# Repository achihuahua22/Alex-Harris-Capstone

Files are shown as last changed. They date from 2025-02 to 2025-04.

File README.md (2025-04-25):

# Alex Harris Capstone: Low Cost Device for Laboratory Equipment Integration
 _This project is a Raspberry Pi Hat that is intended to receive inputs from Self-Driving-Laboratory equipment and utilize the raspberry pi to publish device data onto the network.
This repository contains all of the schematics, documentation, and code necessary to build this device._

This project builds on an-ven’s [graspib](https://github.com/an-ven/graspib) project by adding more RS232 support and a UART breakout pin. 

It also utilizes the [Linux GPIB package](https://linux-gpib.sourceforge.io)

Currently, this device supports UART, RS232, and GPIB. 

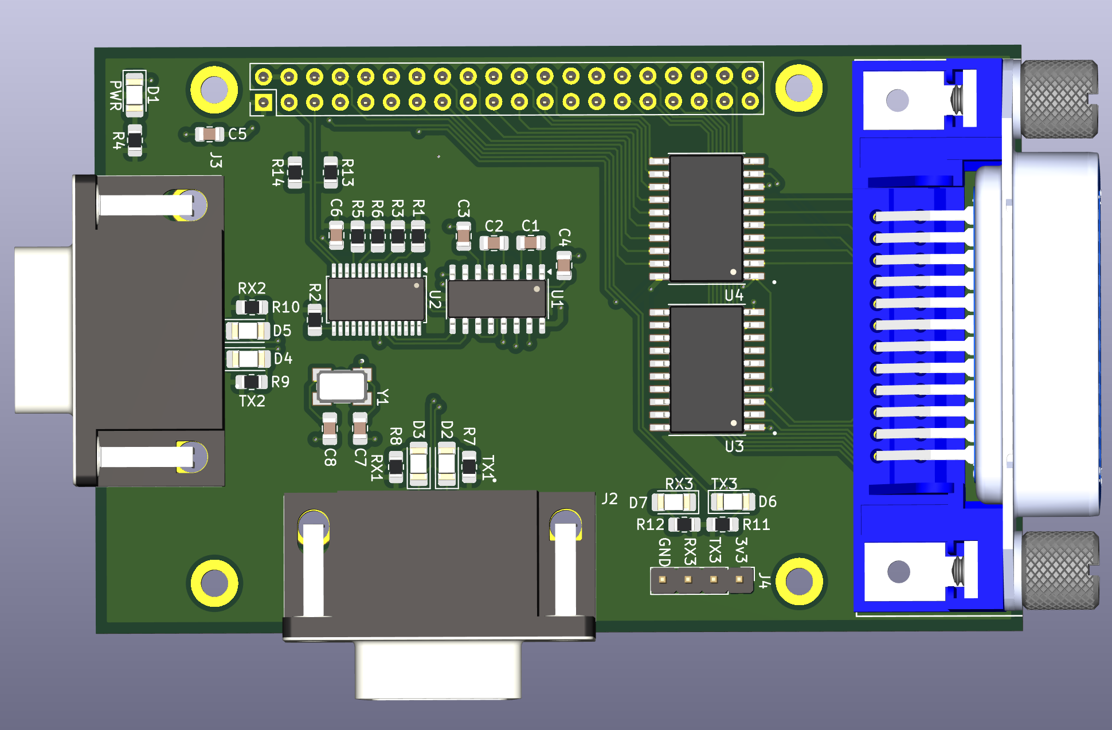
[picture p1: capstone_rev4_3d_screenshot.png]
3d model of pcb


If you want to make one yourself, the files are [here](capstone_cad_rev4)

## Introduction
This project is a Raspberry Pi Hat that is intended to 
improve self driving lab connectivity and modularity 
by allowing researchers to integrate multiple lab 
devices into their networks. I worked with Dr. Taylor 
Sparks' self-driving laboratory (SDL) to develop a 
device to more easily network with lab equipment. 
A self-driving laboratory is a laboratory where
everything from specimen handling, experiments, 
and decision making is fully automated to 
accelerate research [1]. This device intends to be an 
easy-to-use device for networking and save 
researchers money. To make a device “easy to use” I 
wanted to work with hardware that researchers are 
familiar with. This led to me choosing to design a 
board that attaches to a Raspberry Pi. 
I chose to use a Raspberry Pi based solution
because of its prevalence in the research space. 
Many pieces of university research level lab 
equipment have very little interconnection due to 
the age of the device or the type of communication 
protocol. Another issue is that products can use 
proprietary connection methods, which makes the 
task of developing an interconnected SDL very 
difficult [2]. I wanted to develop a device that can 
put data collected by lab equipment onto the 
network using a Raspberry Pi and a circuit board 
that sits on top of the Pi to handle the 
communications.

## Design
### Methods
I began with researching similar solutions to this 
problem, and the two options were a series of adapter 
dongles, or a device that interfaces with a single board 
computer to allow for communication. I chose this 
method as it would be easiest for the end user to have a 
single device that handles lab equipment connectivity.
I started by purchasing pre-built adapter components 
and build a breadboard analog of the final device. This 
device consisted of RS232 adapters and a serial 
expansion board for a Raspberry Pi. With this, I was able 
to test the idea of sending device data over the network 
using ROS and the python socket library.

### Results
I designed a circuit board that could serve as an add on 
that connected to the Raspberry Pi’s GPIO port. To 
expand the capability of the device, a GPIB connection
was added, taking advantage of the open-source Linux 
GPIB package [3]. GPIB is a very common protocol with 
adapters often costing hundreds of dollars.
The board was manufactured by JLCPCB, hand 
assembled, revised, and tested thoroughly. A GitHub 
repository was maintained throughout the project 
detailing hardware and software setup instructions.
The low-cost goal was achieved with the total cost being 
around $40 for the entire device excluding shipping

### Conclusions
Improvements of the Linux GPIB library are needed to 
facilitate easy setup of hardware and improved 
compatibility with the IEEE-488 standard.
Future works should expand on the software for using 
the Raspberry Pi to communicate over the local 
network. Possibly a user interface to improve ease of 
use
Future works should also investigate more permanent, 
universal communication protocols to improve 
laboratory equipment integration.

### Communication Protocols
While there are many communication protocols used in laboratory equipment, a few come up most often when looking at the back of devices in labs around my university. Some of these include:

1. RS232
2. CAN (CAN-FD, etc.)
3. GPIB
4. USB
5. UART
6. HPIB
7. Ethernet

Obviously, it is not possible to develop a device to encompass every existing communication protocol, so I chose three that were most necessary to our SDL and were most feasible with the constraint of a Raspberry Pi powered device. The three protocols I chose were RS232, UART, and GPIB. I chose each of these for the following reasons:
#### _UART_
I chose UART because of its prevalence in open-source projects such as the OpenTrickler, a powder dispensing device that we are using in our SDL. UART is also a simple protocol to implement as it only requires four pins: 3v3, TX, RX, and GND. The end user can configure the Baud rate, parity or stop bits in software. I believe that including this communication allows for other SDLs to integrate their own custom devices and not have to design for network capabilities if they choose to use my device. 
#### _RS232_
I chose RS232 because it was very prevalent in older equipment in our lab such as the Fischer Scientific Analytical Scale, and some open-source devices such as the OpenRAMAN, a laser spectroscopy device for materials classification. While RS232 is an old communication protocol, it is still useful for simple communication of commands. 
#### _GPIB_
Lastly, I chose GPIB because it was also extremely prevalent in many types of laboratory equipment such as multimeters, spectrum analyzers, and other devices. The issue that many laboratories face with GPIB enabled devices is that adapters such as GPIB to USB can cost more than $1,000 and can only communicate with proprietary software. This can render perfectly usable lab equipment almost completely useless in terms of automation or remote data collection.

The following are protocols I didn't choose, future works could consider adding them.

#### _CAN_
I didn’t choose CAN or any of its variants (CAN, CAN-FD, CAN-XL) because it has too many variants to effectively develop a multipurpose product that could encompass of CAN. The differential pair nature of CAN also makes it difficult to develop for.
#### _USB_
I didn’t choose USB because of its complication with drivers, enumeration, host/peripheral, and all the headaches that come with that. In addition to this, a Raspberry Pi does not have the same driver setup as a normal computer which makes implementation difficult when this problem can be solved with a computer and a USB hub.
#### _HPIB_
I didn’t choose HPIB because of the general nature of GPIB (General Purpose Interface Bus) and how HPIB is limited to Hewlett-Packard devices, and that does not make sense with the intent of this project.
#### _Ethernet_
I didn’t choose Ethernet because it also defeats the purpose of this project. The Raspberry Pi used for this project has Ethernet connection capabilities, allowing me to develop a device that just handles the communications between the laboratory equipment and the Pi, reducing cost and complexity.

## Device Assembly
### PCB Manufacturing
At the time of writing, JLCPCB is a very good option for low cost PCB manufacturing. You can get 5 boards for roughly $4 not including shipping. All you need to do is zip these [Gerber Files](https://github.com/achihuahua22/Alex-Harris-Capstone/tree/main/capstone_rev4_gerbers), go to JLCPCB.com, click "upload gerbers" and choose the zipped file. Everything else should populate automatically. You don't need to do any configuration besides choosing the "Lead Free HASL" for a lead free surface finish on the pcb. Feel free to order a stencil as it might make surface mount soldering easier, not required though.

### Parts
Here is the [BOM](https://github.com/achihuahua22/Alex-Harris-Capstone/blob/main/bill_of_materials/senior_capstone_bom_rev4.csv) for the pcb components
   - Unfortunately, all of the components except for item 15 (SN75161BDW) can be purchased from Digikey, the remaining component can be purchased from Mouser
   - In addition, I would recommend M2.5 standoffs to support the board on top of the raspberry pi
   - Solder paste and Heat Gun is recommended for the Surface Mount components as the Resistors, Capacitors, and LED's

### Building
I would recommend using solder paste and a heat gun for installing the small surface mount components such as the resistors, capacitors, crystal and LED's and installing the components in the following order:
1. Resistors (R1-R12)
2. Crystal Oscillator (Y1)
3. Capacitors (C1-C8)
4. LED's (D1-D7) (*pay attention to the orientation of the LED!*)
   - The open part of the rectangle is the anode, the closed part is the cathode
5. Integrated Circuits (U1-U4) (In order of 1 to 4 is easiest)
6. Connectors

It is not required to install the components in this order, but is is easier to install the smaller components first so you don't have to navigate around the large connectors or IC's.
   
## Setup
1. Setup fresh install of [raspberry pi os](https://www.raspberrypi.com/software/)
2. Configure your network, password, etc to your liking
3. Download Provided [files](https://github.com/achihuahua22/Alex-Harris-Capstone/blob/main/send_to_network.c) to send data to network
4. From [graspib documentation](https://github.com/an-ven/graspib/tree/main) : 

   Install build tools and dependencies
   - Build tools: ```$ sudo apt install build-essential autoconf automake libtool flex bison```
   - RPi kernel headers: ```$ sudo apt install raspberrypi-kernel-headers```
   - Python3 headers: ```$ sudo apt install python3-dev```

    Download linux-gpib source files
   - Get release archives (4.3.4 or later) from https://sourceforge.net/projects/linux-gpib/files
   - or get the latest source from https://sourceforge.net/p/linux-gpib/code/HEAD/tree/

   Build and install kernel drivers
   - Enter linux-gpib-kernel directory ```$ cd linux-gpib-src-dir/linux-gpib-kernel```
   - Build kernel module by running make ```$ make```
   - Install kernel module ```$ sudo make install```
   - Update kernel module list ```$ sudo depmod -a```
   - Load gpib_bitbang kernel module ```$ sudo modprobe gpib_bitbang```
   - Now there should be some gpib* devices in /dev
   - Make the module loads on boot by adding gpib_bitbang line to /etc/modules-load.d/modules.conf

   When Raspberry Pi OS kernel gets upgraded, linux-gpib kernel module also needs to be rebuilt and reinstalled. 
   Basically just repeat above make and make install steps when kernel gets upgraded

   Build and install user space tools
   - Enter linux-gpib-user directory: ```$ cd linux-gpib-src-dir/linux-gpib-user```
   - If building from svn checkout first run bootstrap script: $ ./bootstrap
   - Run configure script: ```$ ./configure (run $ ./configure --help to list additional options)```
   - Build user space tools by running make: $ make
   - Install user space tools: ```$ sudo make install```
   - Make sure that shared library directory (default: /usr/local/lib/) is listed in: /etc/ld.so.conf.d/
   - Then run: $ sudo ldconfig

   Configure GPIB interface
   - Open gpib.conf configuration file $ sudo nano /usr/local/etc/gpib.conf (default location)
   - Set board_type = "gpib_bitbang" and other relevant settings (for details refer to included gpib.conf file, linux-gpib documentetion and included template file linux-gpib-src-dir/linux-gpib-user/util/template/gpib.conf)
   - Run gpib_config so the driver reads the configuration file $ sudo gpib_config --minor 0
   - Make the last command execute on every startup using crontab entry:
   - Edit crontab for root user: ```$ sudo crontab -e```
   - Add line the following line to cron tab file: @reboot /usr/local/sbin/gpib_config --minor 0
   - Enable non root users to use GPIB interface without sudo
   - Add new gpib system group: ```$ sudo groupadd -r gpib```
   - Append your_user_name to gpib supplementary group: ```$ sudo usermod -a -G gpib your_user_name```
   - Create /etc/udev/rules.d/99-gpib.rules file and add line: SUBSYSTEM=="gpib_common", GROUP="gpib", MODE="0660"

Reboot system to apply changes (udevadm utility can also be used, but reboot is dead simple to remember)
Test by running ibtest without sudo

5. Run and do the following to enable the I2C interface:
   - Open a terminal and run ```sudo raspi-config```
   - Select "Interface Options"
   - Select "P5 I2C"
   - It will prompt you with "Would you like the ARM I2C interface to be enabled?" *select yes*
   - Then it will prompt you to reboot *select yes*
   - After reboot, open another terminal and run ```sudo apt-get update``` and ```sudo apt-get install -y python3-smbus i2c-tools```
   - Finally shut down the raspberry pi with ```sudo halt```
   - Wait 10 seconds unplug power and restart
6. Run the following in the raspberry pi os terminal to configure serial and socket:
   
   - Update package list ```sudo apt update```
   - Install socket ```python3 -m pip install socket```
   - Install pySerial ```python3 -m pip install pyserial```
   - Install WiringPi ```sudo apt install wiringpi```
   - Install build tools ```sudo apt install build-essential```

7. See following [instructions](https://github.com/an-ven/graspib/tree/main) from grasPIB repository to configure the raspberry pi for GPIB
8. Configure Baud rate, IP, and I2C addresses in code

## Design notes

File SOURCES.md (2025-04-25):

- [1] C. C. R. and Dr. C. P. B. Benjamin P. MacLeod, “Ada: A self-driving laboratory for Clean Energy Technologies,” Inside Unmanned Systems, 
https://insideunmannedsystems.com/ada-a-self-driving-laboratory-for-clean-energy-technologies/.
- [2] P. M. Maffettone et al., “What is missing in Autonomous Discovery: Open challenges for the community,” Digital Discovery, 
https://pubs.rsc.org/en/content/articlehtml/2023/dd/d3dd00143a. 
- [3] F.M. Hess, “Linix GPIB Package,” Sourceforge,
https://linux-gpib.sourceforge.io/

Previous Works:
- http://elektronomikon.org/

- https://github.com/an-ven/graspib

Python Socket Library
- https://docs.python.org/3/library/socket.html#creating-sockets

GPIB Fundamentals
- https://helpfiles.keysight.com/csg/N52xxB/Programming/Learning_about_GPIB/GP-IB_Fundamentals.htm

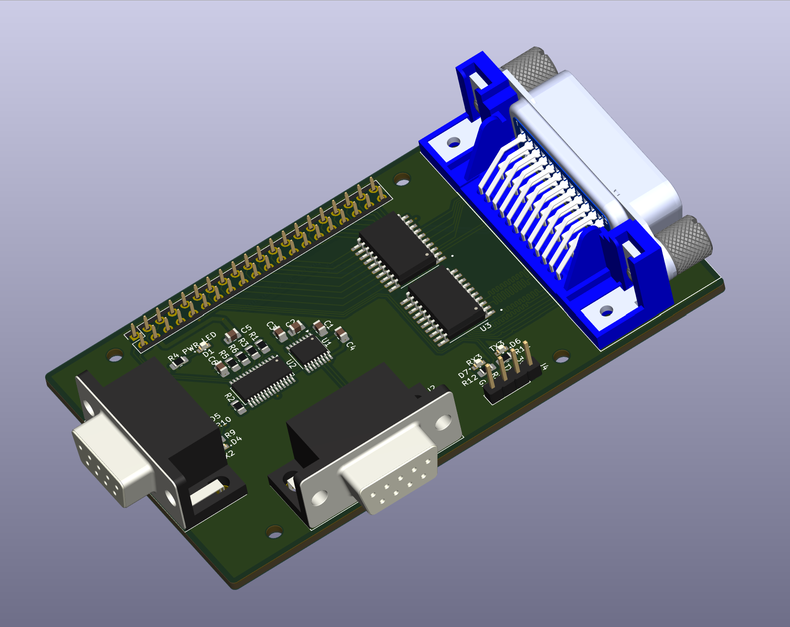
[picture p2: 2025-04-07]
capstone_rev3_3d_screenshot.png

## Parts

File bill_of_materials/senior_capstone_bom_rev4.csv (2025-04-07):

Index | Manufacturer Part Number | Manufacturer Name | Description | References | Requested Quantity 1 | Pack Quantity 1 | Pack Type 1 | Digi-Key Part Number 1 | Unit Price 1 | Extended Price 1 | Minimum Order Quantity 1 | Datasheet | Product Notes
1 | 22284040 | Molex | CONN HEADER VERT 4POS 2.54MM | J4 | 1 | 1 | Bulk | WM50014-04-ND | 0.3 | $0.30 | 1 | https://www.molex.com/pdm_docs/sd/022284040_sd.pdf
2 | RC0805FR-071KL | YAGEO | RES 1K OHM 1% 1/8W 0805 | R2, R3, R4, R5, R6, R7, R8, R9, R10, R11, R12 | 11 | 11 | Cut Tape (CT) | 311-1.00KCRCT-ND | 0.012 | $0.13 | 1 | https://www.yageo.com/upload/media/product/products/datasheet/rchip/PYu-RC_Group_51_RoHS_L_12.pdf
3 | 08055C104J4T2A | KYOCERA AVX | CAP CER 0.1UF 50V X7R 0805 | C1-C6 | 7 | 7 | Cut Tape (CT) | 478-KAM21BR71H104JTCT-ND | 0.18 | $1.26 | 1 | https://datasheets.kyocera-avx.com/AutoMLCC.pdf
4 | SC16IS752IPW,112 | NXP USA Inc. | IC UART DUAL 12C/SPI 28TSSOP | U2 | 1 | 1 | Tube | 568-4016-5-ND | 4.48 | $4.48 | 1 | https://www.nxp.com/docs/en/data-sheet/SC16IS752_SC16IS762.pdf
5 | SN75160BDW | Texas Instruments | IC TRANSCEIVER HALF 8/8 20SOIC | U3 | 1 | 1 | Tube | 296-6844-5-ND | 3.39 | $3.39 | 1 | https://www.ti.com/general/docs/suppproductinfo.tsp?distId=10
6 | CIB24SRA | L-com | CONNECTOR GPIB R/A FEMALE | J5 | 1 | 1 | Bag | 5073-CIB24SRA-ND | 17.1 | $17.10 | 1 | https://www.l-com.com/images/downloadables/2D/CIB24SRA_2D.pdf
7 | PRT-16764 | SparkFun Electronics | EXTENDED GPIO FEMALE HEADER - 2X | J1 | 1 | 1 | Bulk | 1568-PRT-16764-ND | 2.25 | $2.25 | 1 | https://cdn.sparkfun.com/assets/0/8/d/b/2/DS-16764-2_X_20_Pin_Extended_GPIO_Header_-_Female_-_13.5mm_9.80mm.pdf
8 | 405C35B14M74560 | CTS-Frequency Controls | CRYSTAL 14.7456MHZ 13PF SMD | Y1 | 1 | 1 | Cut Tape (CT) | CTX644CT-ND | 0.84 | $0.84 | 1 | https://www.ctscorp.com/Files/DataSheets/Passives/FCP/Crystals/crystals-405-datasheet.pdf
9 | LD09P13A4GX00LF | Amphenol ICC (FCI) | CONN D-SUB PLUG 9POS R/A SOLDER | J2,J3 | 2 | 2 | Tray | 609-5183-ND | 1.23 | $2.46 | 1 | https://cdn.amphenol-cs.com/media/wysiwyg/files/documentation/datasheet/inputoutput/io_dsub_brochure.pdf
10 | CC0805JRNPO9BN360 | YAGEO | CAP CER 36PF 50V C0G/NPO 0805 | C7,C8 | 2 | 2 | Cut Tape (CT) | 311-4236-1-ND | 0.12 | $0.24 | 1 | https://www.yageo.com/en/Chart/Download/pdf/CC0805JRNPO9BN360
11 | MAX3232CDR | Texas Instruments | IC TRANSCEIVER FULL 2/2 16SOIC | U1 | 1 | 1 | Cut Tape (CT) | 296-13094-1-ND | 0.98 | $0.98 | 1 | https://www.ti.com/lit/ds/symlink/max3232.pdf
12 | LTST-C150KRKT | Lite-On Inc. | LED RED CLEAR 1206 SMD | D1 | 1 | 1 | Cut Tape (CT) | 160-1405-1-ND | 0.18 | $0.18 | 1 | https://optoelectronics.liteon.com/upload/download/DS-22-99-0149/LTST-C150KRKT.pdf
13 | LTST-C150GKT | Lite-On Inc. | LED GREEN CLEAR 1206 SMD | D2, D3, D4, D5, D6, D7 | 6 | 6 | Cut Tape (CT) | 160-1169-1-ND | 0.17 | $1.02 | 1 | https://optoelectronics.liteon.com/upload/download/DS-22-98-0004/LTST-C150GKT.pdf
14 | RMCF0805FT10K0 | Stackpole Electronics Inc | RES 10K OHM 1% 1/8W 0805 | R1,R13,R14 | 4 | 4 | Cut Tape (CT) | RMCF0805FT10K0CT-ND | 0.1 | $0.40 | 1 | https://www.seielect.com/catalog/sei-rmcf_rmcp.pdf
15 | SN75161BDW | 296-6846-5-ND | IC TRANSCEIVER HALF 8/8 20SOIC | U4 | 1
 |  |  |  |  |  | $35.81

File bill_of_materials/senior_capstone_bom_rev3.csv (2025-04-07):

Manufacturer # | Supplier # | References | Label | Quantity | Unit Price | Total Price | Link
PRT-21570 | 474-PRT-21570 | J1 | GPIO, PinSocket_2x20_P2.54mm_Vertical | 1 | $1.95 | $1.95 | https://www.mouser.com/ProductDetail/SparkFun/PRT-21570?qs=dbcCsuKDzFXE3Ci1AQT/Bw%3D%3D&mgh=1&gQT=0
22284040 | WM50014-04-ND | J4 | UART, PinHeader_1x04_P2.54mm_Vertical | 2 | $0.30 | $0.60 | https://www.digikey.com/en/products/detail/molex/0022284040/313789
L77SDE09SA4CH3FC309 | 523-SDE09SA4CH3FC309 | J2,J3 | D-Sub Standard Connectors D-SUB | 2 | $2.64 | $5.28 | https://www.mouser.com/ProductDetail/Amphenol-Commercial-Products/L77SDE09SA4CH3FC309?qs=mq7kV%2Fq8lk5ORILqzEGv%252Bw%3D%3D
150060RS75000 | 732-4978-2-ND - Tape & Reel (TR) | D1 | LED RED CLEAR 0603 SMD | 1 | $0.14 | $0.14 | https://www.digikey.com/en/products/detail/w%C3%BCrth-elektronik/150060RS75000/4489901
150060VS75000 | 732-4980-2-ND | D2, D3, D4, D5, D6, D7 | Green 570nm LED Indication - Discrete 2V 0603 (1608 Metric) | 8 | $0.14 | $1.12 | https://www.digikey.com/en/products/detail/w%C3%BCrth-elektronik/150060VS75000/4489906
RC0805FR-071KL | 311-1.00KCRTR-ND | R2, R3, R4, R5, R6, R7, R8, R9, R10, R11, R12 | Thick Film Resistors - SMD 0805 1Kohms 125mW 1% | 11 | $0.10 | $1.10 | https://www.digikey.com/en/products/detail/yageo/RC0805FR-071KL/727444
ERJ-6RBD1002V | 667-ERJ-6RBD1002V | R1 | Thick Film Resistors - SMD 0805 10Kohms 0.5% AEC-Q200 | 1 | $0.18 | $0.18 | https://www.mouser.com/ProductDetail/Panasonic/ERJ-6RBD1002V?qs=18kBAoNi3c%2F5OpcgdPnLzA%3D%3D
KAM21BR71H104JT | 581-KAM21BR71H104JT | C1-C12 | Multilayer Ceramic Capacitors MLCC - SMD/SMT 50V .1uF X7R 0805 5% AEC-Q200 | 12 | $0.20 | $2.40 | https://www.mouser.com/ProductDetail/KYOCERA-AVX/KAM21BR71H104JT?qs=Jm2GQyTW%2Fbic6Zk4McEt6w%3D%3D
MAX3232CPWR | 595-MAX3232CPWR | U1 | RS-232 Interface IC 3-5.5V Mult-Ch RS232 A 595-MAX3232CPW | 1 | $0.80 | $0.80 | https://www.mouser.com/ProductDetail/Texas-Instruments/MAX3232CPWR?qs=bkMXpVdiF40tDMAEI%2F4vWA%3D%3D
SC16IS752IPW | 568-11844-2-ND | U2 | IC UART DUAL I2C/SPI 32-HVQFN | 1 | $4.57 | $4.57 | https://www.digikey.com/en/products/detail/nxp-usa-inc/SC16IS752IPW-128/1158200
SN75160BDW | 296-6844-5-ND | U3 | IC TRANSCEIVER HALF 8/8 20SOIC | 1 | $3.11 | $3.11 | https://www.digikey.com/en/products/detail/texas-instruments/SN75160BDW/370216
SN75161BDW | 296-6846-5-ND | U4 | IC TRANSCEIVER HALF 8/8 20SOIC | 1 | $1.77 | $1.77 | https://www.digikey.com/en/products/detail/texas-instruments/SN75161BDW/370218
CIB24SRA | CIB24SRA | J5 | GPIB Connector | 1 | $12.79 | $12.79 | https://www.l-com.com/ieee-488-gpib-female-ieee-488-connector-right-angle-pc-terminals
 |  |  |  |  |  | $35.81

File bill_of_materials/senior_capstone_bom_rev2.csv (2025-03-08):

Manufacturer # | Supplier # | References | Label | Quantity | Unit Price | Total Price | Link
PRT-21570 | 474-PRT-21570 | J1 | GPIO, PinSocket_2x20_P2.54mm_Vertical | 1 | $1.95 | $1.95 | https://www.mouser.com/ProductDetail/SparkFun/PRT-21570?qs=dbcCsuKDzFXE3Ci1AQT/Bw%3D%3D&mgh=1&gQT=0
22284040 | WM50014-04-ND | J4,J5 | UART, PinHeader_1x04_P2.54mm_Vertical | 2 | $0.30 | $0.60 | https://www.digikey.com/en/products/detail/molex/0022284040/313789
L77SDE09SA4CH3FC309 | 523-SDE09SA4CH3FC309 | J2, J3 | D-Sub Standard Connectors D-SUB | 2 | $2.64 | $5.28 | https://www.mouser.com/ProductDetail/Amphenol-Commercial-Products/L77SDE09SA4CH3FC309?qs=mq7kV%2Fq8lk5ORILqzEGv%252Bw%3D%3D
150060RS75000 | 732-4978-2-ND - Tape & Reel (TR) | D1 | LED RED CLEAR 0603 SMD | 1 | $0.14 | $0.14 | https://www.digikey.com/en/products/detail/w%C3%BCrth-elektronik/150060RS75000/4489901
150060VS75000 | 732-4980-2-ND | D2-D9 | Green 570nm LED Indication - Discrete 2V 0603 (1608 Metric) | 8 | $0.14 | $1.12 | https://www.digikey.com/en/products/detail/w%C3%BCrth-elektronik/150060VS75000/4489906
RC0805FR-071KL | 311-1.00KCRTR-ND | R2-R12, R14-R18 | Thick Film Resistors - SMD 0805 1Kohms 125mW 1% | 16 | $0.10 | $1.60 | https://www.digikey.com/en/products/detail/yageo/RC0805FR-071KL/727444
ERJ-6RBD1002V | 667-ERJ-6RBD1002V | R1, R13 | Thick Film Resistors - SMD 0805 10Kohms 0.5% AEC-Q200 | 2 | $0.18 | $0.36 | https://www.mouser.com/ProductDetail/Panasonic/ERJ-6RBD1002V?qs=18kBAoNi3c%2F5OpcgdPnLzA%3D%3D
KAM21BR71H104JT | 581-KAM21BR71H104JT | C1-C12 | Multilayer Ceramic Capacitors MLCC - SMD/SMT 50V .1uF X7R 0805 5% AEC-Q200 | 12 | $0.20 | $2.40 | https://www.mouser.com/ProductDetail/KYOCERA-AVX/KAM21BR71H104JT?qs=Jm2GQyTW%2Fbic6Zk4McEt6w%3D%3D
MAX3232CPWR | 595-MAX3232CPWR | U2,U4 | RS-232 Interface IC 3-5.5V Mult-Ch RS232 A 595-MAX3232CPW | 2 | $0.80 | $1.60 | https://www.mouser.com/ProductDetail/Texas-Instruments/MAX3232CPWR?qs=bkMXpVdiF40tDMAEI%2F4vWA%3D%3D
SC16IS752IBS,151 | 568-2236-ND | U1,U5 | IC UART DUAL I2C/SPI 32-HVQFN | 2 | $5.10 | $10.20 | https://www.digikey.com/en/products/detail/nxp-usa-inc/SC16IS752IBS-151/946245
 |  |  |  |  |  | $25.25

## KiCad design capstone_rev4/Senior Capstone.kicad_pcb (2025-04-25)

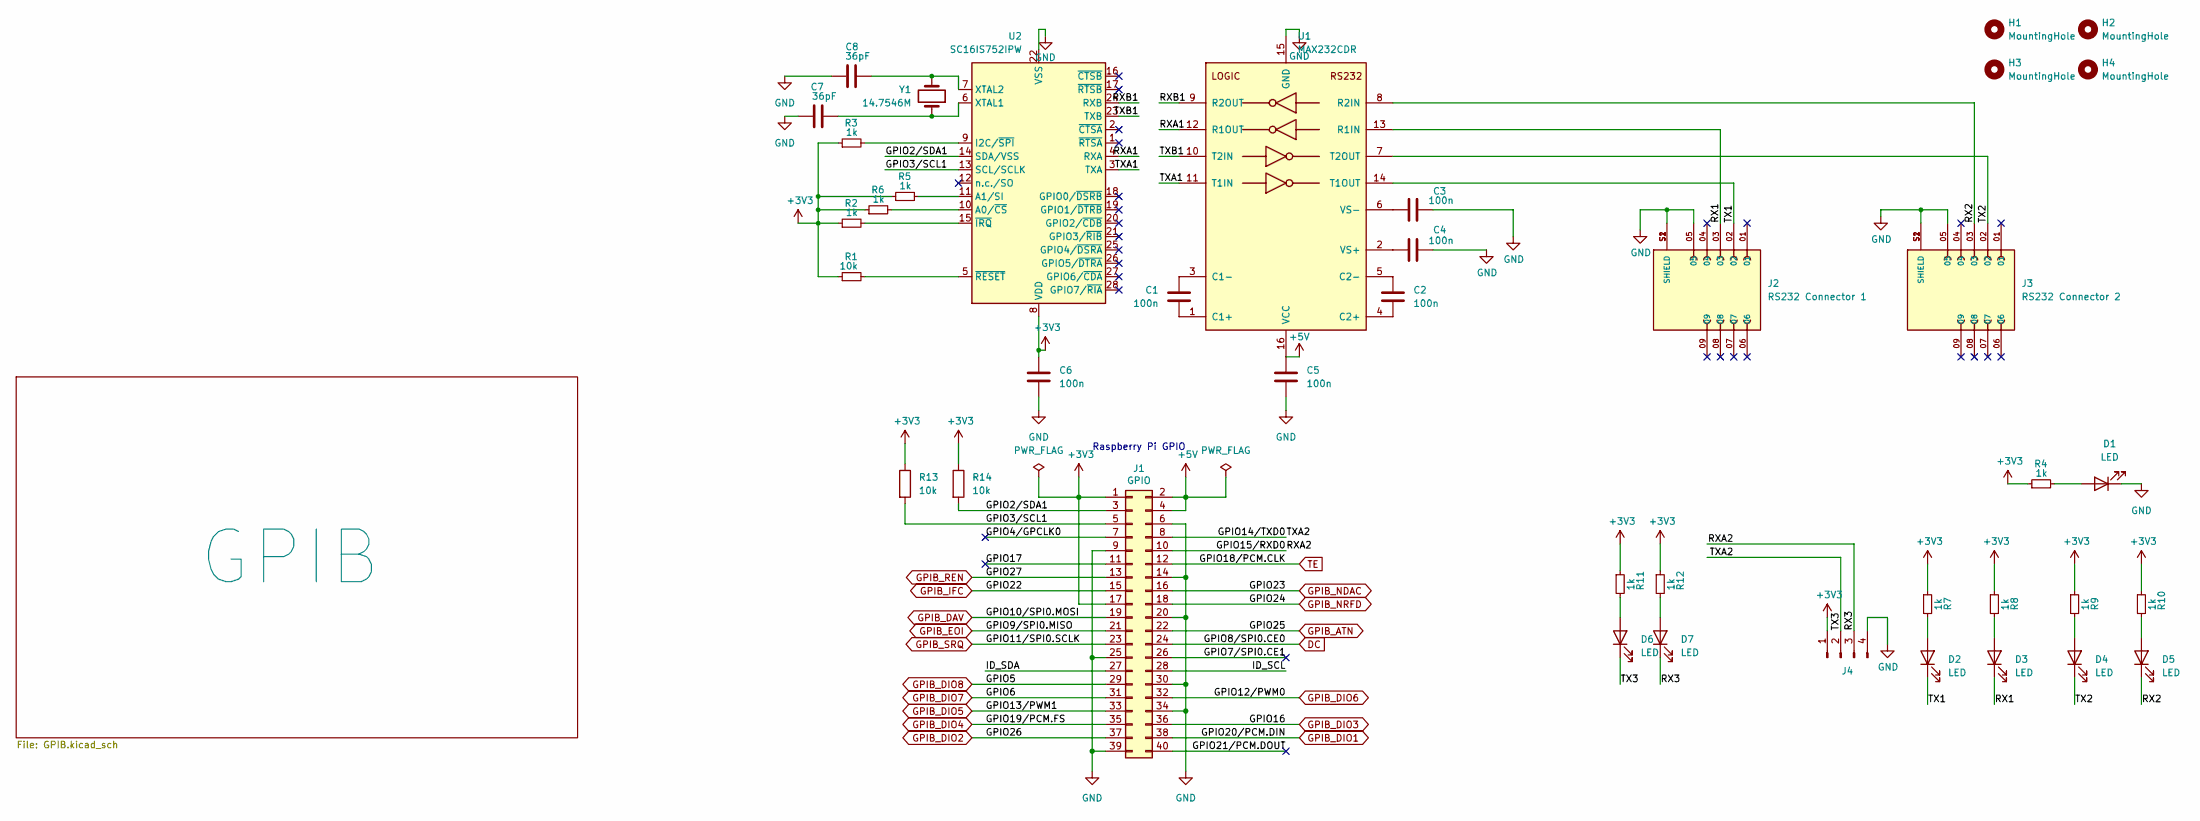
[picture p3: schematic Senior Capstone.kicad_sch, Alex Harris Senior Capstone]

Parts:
C1, C2, C3, C4, C5, C6: 100n; C_0805_2012Metric
C7, C8: 36pF; C_0805_2012Metric_Pad1.18x1.45mm_HandSolder
D1, D2, D3, D4, D5, D6, D7: LED; LED_1206_3216Metric_Pad1.42x1.75mm_HandSolder
H1, H2, H3, H4: MountingHole; MountingHole_2.7mm_M2.5_DIN965_Pad_TopBottom
J1: GPIO; PinSocket_2x20_P2.54mm_Vertical
J2: RS232 Connector 1; AMPHENOL_L77SDE09SA4CH3FC309; PARTREV 1
J3: RS232 Connector 2; AMPHENOL_L77SDE09SA4CH3FC309; PARTREV 1
J4: Conn_01x04_Pin; PinHeader_1x04_P2.54mm_Vertical
R1, R13, R14: 10k; R_0805_2012Metric_Pad1.20x1.40mm_HandSolder
R2, R3, R4, R5, R6, R7, R8, R9, R10, R11, R12: 1k; R_0805_2012Metric_Pad1.20x1.40mm_HandSolder
U1: MAX232CDR; SOIC-16_3.9x9.9mm_P1.27mm
U2: SC16IS752IPW; TSSOP-28_4.4x9.7mm_P0.65mm
Y1: 14.7546M; XTAL_405C35B14M74560

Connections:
+3V3: C6.1, J1.1, J1.17, J4.1, R1.1, R2.1, R3.1, R4.1, R5.1, R6.1, R7.1, R8.1, R9.1, R10.1, R11.1, R12.1, R13.1, R14.1, U2.8 (VDD)
+5V: C5.1, J1.2, J1.4, U1.16 (VCC); also elsewhere on the board
/GPIO2/SDA1: J1.3, R14.2, U2.14 (SDA/VSS)
/GPIO3/SCL1: J1.5, R13.2, U2.13 (SCL/SCLK)
/GPIO4/GPCLK0: J1.7
/GPIO7/SPI0.CE1: J1.26
/GPIO14/TXD0: D6.1 (K), J1.8, J4.2
/GPIO15/RXD0: D7.1 (K), J1.10, J4.3
/GPIO17: J1.11
/GPIO21/PCM.DOUT: J1.40
/ID_SCL: J1.28
/ID_SDA: J1.27
/RX1: D3.1 (K), J2.03, U1.13 (R1IN)
/RX2: D5.1 (K), J3.03, U1.8 (R2IN)
/RXA1: U1.12 (R1OUT), U2.4 (RXA)
/RXB1: U1.9 (R2OUT), U2.24 (RXB)
/TX1: D2.1 (K), J2.02, U1.14 (T1OUT)
/TX2: D4.1 (K), J3.02, U1.7 (T2OUT)
/TXA1: U1.11 (T1IN), U2.3 (TXA)
/TXB1: U1.10 (T2IN), U2.23 (TXB)
DC: J1.24; also elsewhere on the board
GND: C3.2, C4.2, C5.2, C6.2, C7.2, C8.2, D1.1 (K), J1.6, J1.9, J1.14, J1.20, J1.25, J1.30, J1.34, J1.39, J2.05, J2.S1 (SHIELD), J2.S2 (SHIELD), J3.05, J3.S1 (SHIELD), J3.S2 (SHIELD), J4.4, U1.15 (GND), U2.22 (VSS); also elsewhere on the board
GPIB_ATN: J1.22; also elsewhere on the board
GPIB_DAV: J1.19; also elsewhere on the board
GPIB_DIO1: J1.38; also elsewhere on the board
GPIB_DIO2: J1.37; also elsewhere on the board
GPIB_DIO3: J1.36; also elsewhere on the board
GPIB_DIO4: J1.35; also elsewhere on the board
GPIB_DIO5: J1.33; also elsewhere on the board
GPIB_DIO6: J1.32; also elsewhere on the board
GPIB_DIO7: J1.31; also elsewhere on the board
GPIB_DIO8: J1.29; also elsewhere on the board
GPIB_EOI: J1.21; also elsewhere on the board
GPIB_IFC: J1.15; also elsewhere on the board
GPIB_NDAC: J1.16; also elsewhere on the board
GPIB_NRFD: J1.18; also elsewhere on the board
GPIB_REN: J1.13; also elsewhere on the board
GPIB_SRQ: J1.23; also elsewhere on the board
unnamed: D1.2 (A), R4.2
unnamed: D2.2 (A), R7.2
unnamed: D3.2 (A), R8.2
unnamed: D4.2 (A), R9.2
unnamed: D5.2 (A), R10.2
unnamed: D6.2 (A), R11.2
unnamed: D7.2 (A), R12.2
unnamed: C1.2, U1.1 (C1+)
unnamed: C1.1, U1.3 (C1-)
unnamed: C2.2, U1.4 (C2+)
unnamed: C2.1, U1.5 (C2-)
unnamed: C4.1, U1.2 (VS+)
unnamed: C3.1, U1.6 (VS-)
unnamed: R6.2, U2.10 (A0/~CS)
unnamed: R5.2, U2.11 (A1/SI)
unnamed: R3.2, U2.9 (I2C/~SPI)
unnamed: C7.1, U2.6 (XTAL1), Y1.1
unnamed: C8.1, U2.7 (XTAL2), Y1.2
unnamed: R2.2, U2.15 (~IRQ)
unnamed: R1.2, U2.5 (~RESET)
TE: J1.12; also elsewhere on the board

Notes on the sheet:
Raspberry Pi GPIO

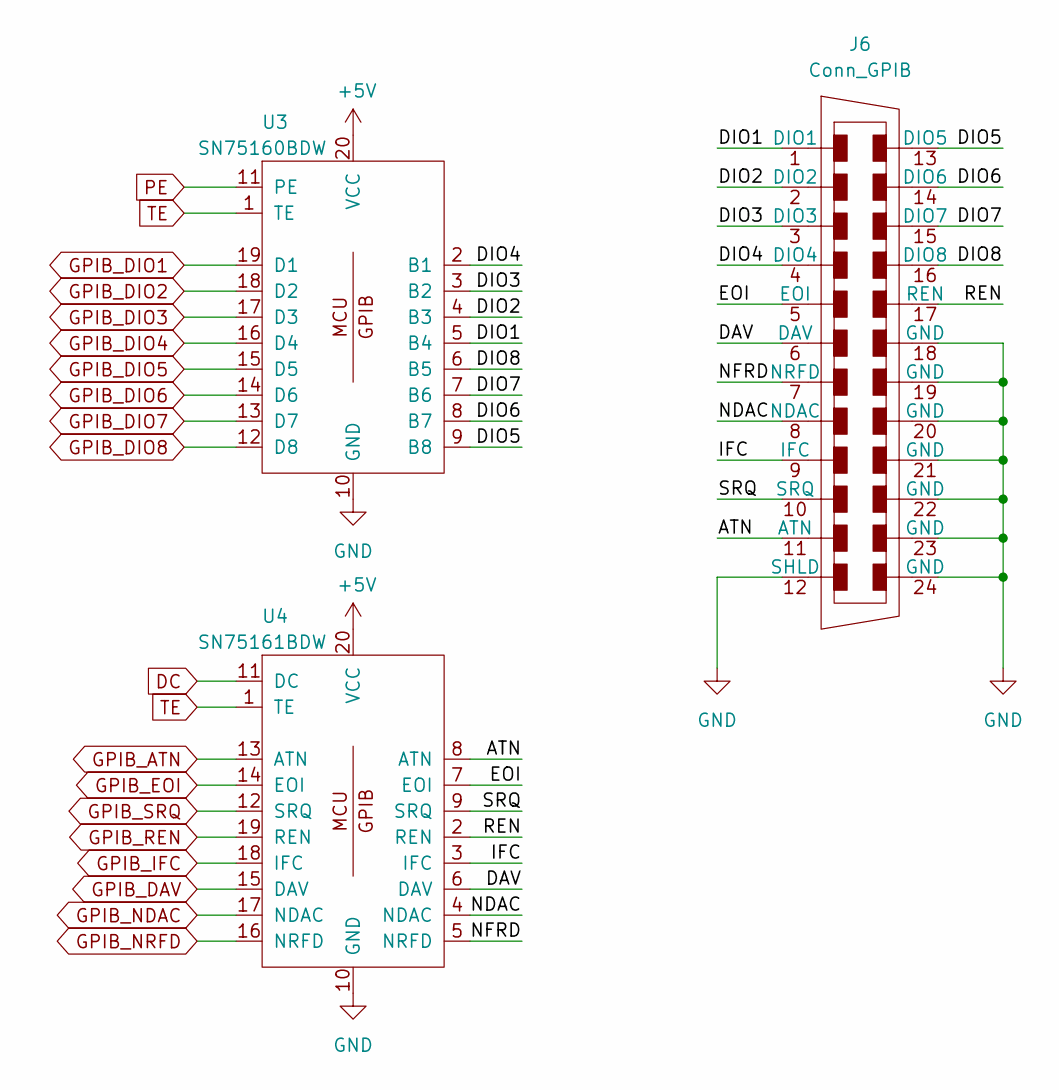
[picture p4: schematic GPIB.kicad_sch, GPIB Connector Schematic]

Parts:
J6: Conn_GPIB; CONN_112-024-113R001_NRC
U3: SN75160BDW; SOIC127P1030X265-20N
U4: SN75161BDW; SOIC127P1030X265-20N

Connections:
+5V: U3.20 (VCC), U4.20 (VCC); also elsewhere on the board
/GPIB/ATN: J6.11 (ATN), U4.8 (ATN)
/GPIB/DAV: J6.6 (DAV), U4.6 (DAV)
/GPIB/DIO1: J6.1 (DIO1), U3.5 (B4)
/GPIB/DIO2: J6.2 (DIO2), U3.4 (B3)
/GPIB/DIO3: J6.3 (DIO3), U3.3 (B2)
/GPIB/DIO4: J6.4 (DIO4), U3.2 (B1)
/GPIB/DIO5: J6.13 (DIO5), U3.9 (B8)
/GPIB/DIO6: J6.14 (DIO6), U3.8 (B7)
/GPIB/DIO7: J6.15 (DIO7), U3.7 (B6)
/GPIB/DIO8: J6.16 (DIO8), U3.6 (B5)
/GPIB/EOI: J6.5 (EOI), U4.7 (EOI)
/GPIB/IFC: J6.9 (IFC), U4.3 (IFC)
/GPIB/NDAC: J6.8 (NDAC), U4.4 (NDAC)
/GPIB/NFRD: J6.7 (NRFD), U4.5 (NRFD)
/GPIB/REN: J6.17 (REN), U4.2 (REN)
/GPIB/SRQ: J6.10 (SRQ), U4.9 (SRQ)
DC: U4.11 (DC); also elsewhere on the board
GND: J6.12 (SHLD), J6.18 (GND), J6.19 (GND), J6.20 (GND), J6.21 (GND), J6.22 (GND), J6.23 (GND), J6.24 (GND), U3.10 (GND), U4.10 (GND); also elsewhere on the board
GPIB_ATN: U4.13 (ATN); also elsewhere on the board
GPIB_DAV: U4.15 (DAV); also elsewhere on the board
GPIB_DIO1: U3.19 (D1); also elsewhere on the board
GPIB_DIO2: U3.18 (D2); also elsewhere on the board
GPIB_DIO3: U3.17 (D3); also elsewhere on the board
GPIB_DIO4: U3.16 (D4); also elsewhere on the board
GPIB_DIO5: U3.15 (D5); also elsewhere on the board
GPIB_DIO6: U3.14 (D6); also elsewhere on the board
GPIB_DIO7: U3.13 (D7); also elsewhere on the board
GPIB_DIO8: U3.12 (D8); also elsewhere on the board
GPIB_EOI: U4.14 (EOI); also elsewhere on the board
GPIB_IFC: U4.18 (IFC); also elsewhere on the board
GPIB_NDAC: U4.17 (NDAC); also elsewhere on the board
GPIB_NRFD: U4.16 (NRFD); also elsewhere on the board
GPIB_REN: U4.19 (REN); also elsewhere on the board
GPIB_SRQ: U4.12 (SRQ); also elsewhere on the board
PE: U3.11 (PE)
TE: U3.1 (TE), U4.1 (TE); also elsewhere on the board

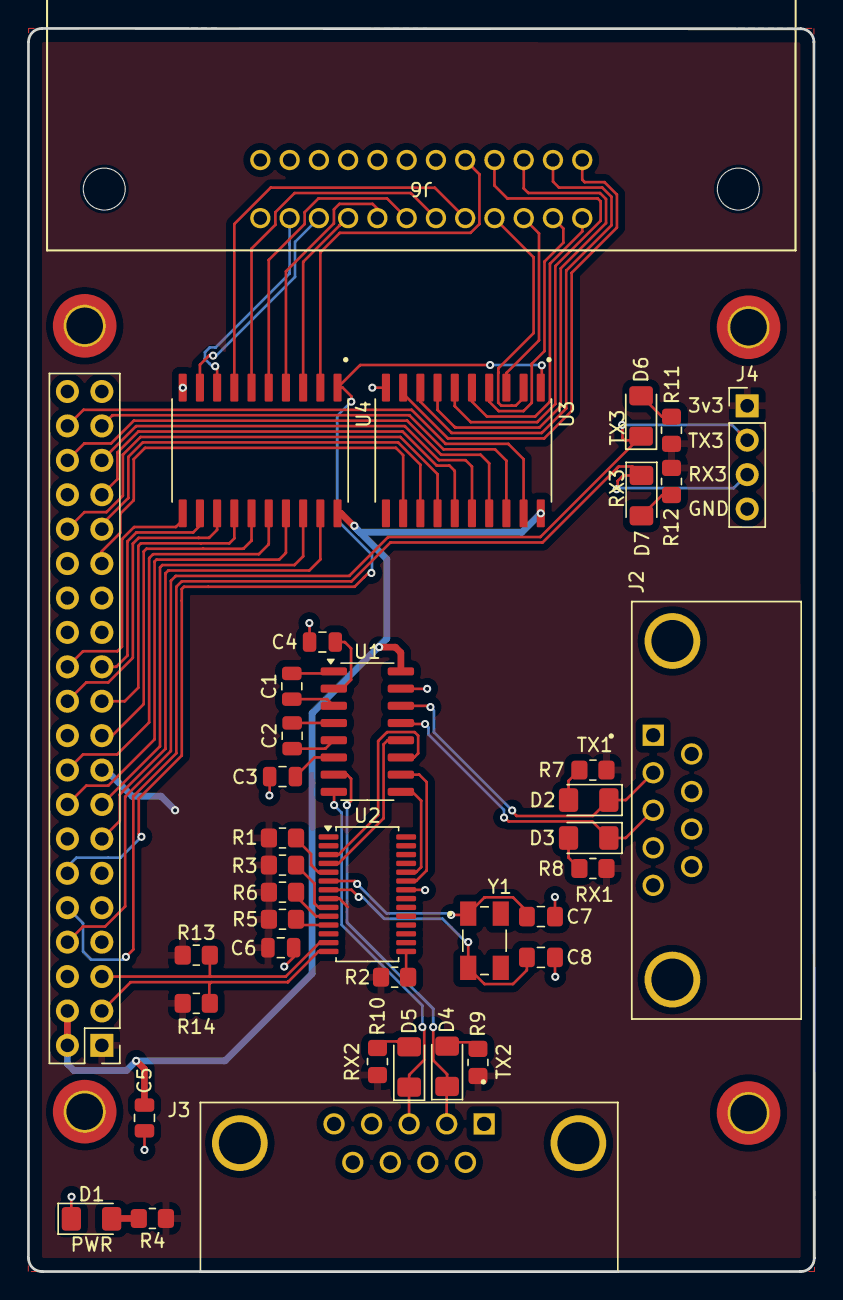
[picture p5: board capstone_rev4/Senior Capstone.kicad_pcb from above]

Board: 2 copper layers, 58.0 x 91.8 mm, 43 parts (0 on the bottom side), 69 nets.

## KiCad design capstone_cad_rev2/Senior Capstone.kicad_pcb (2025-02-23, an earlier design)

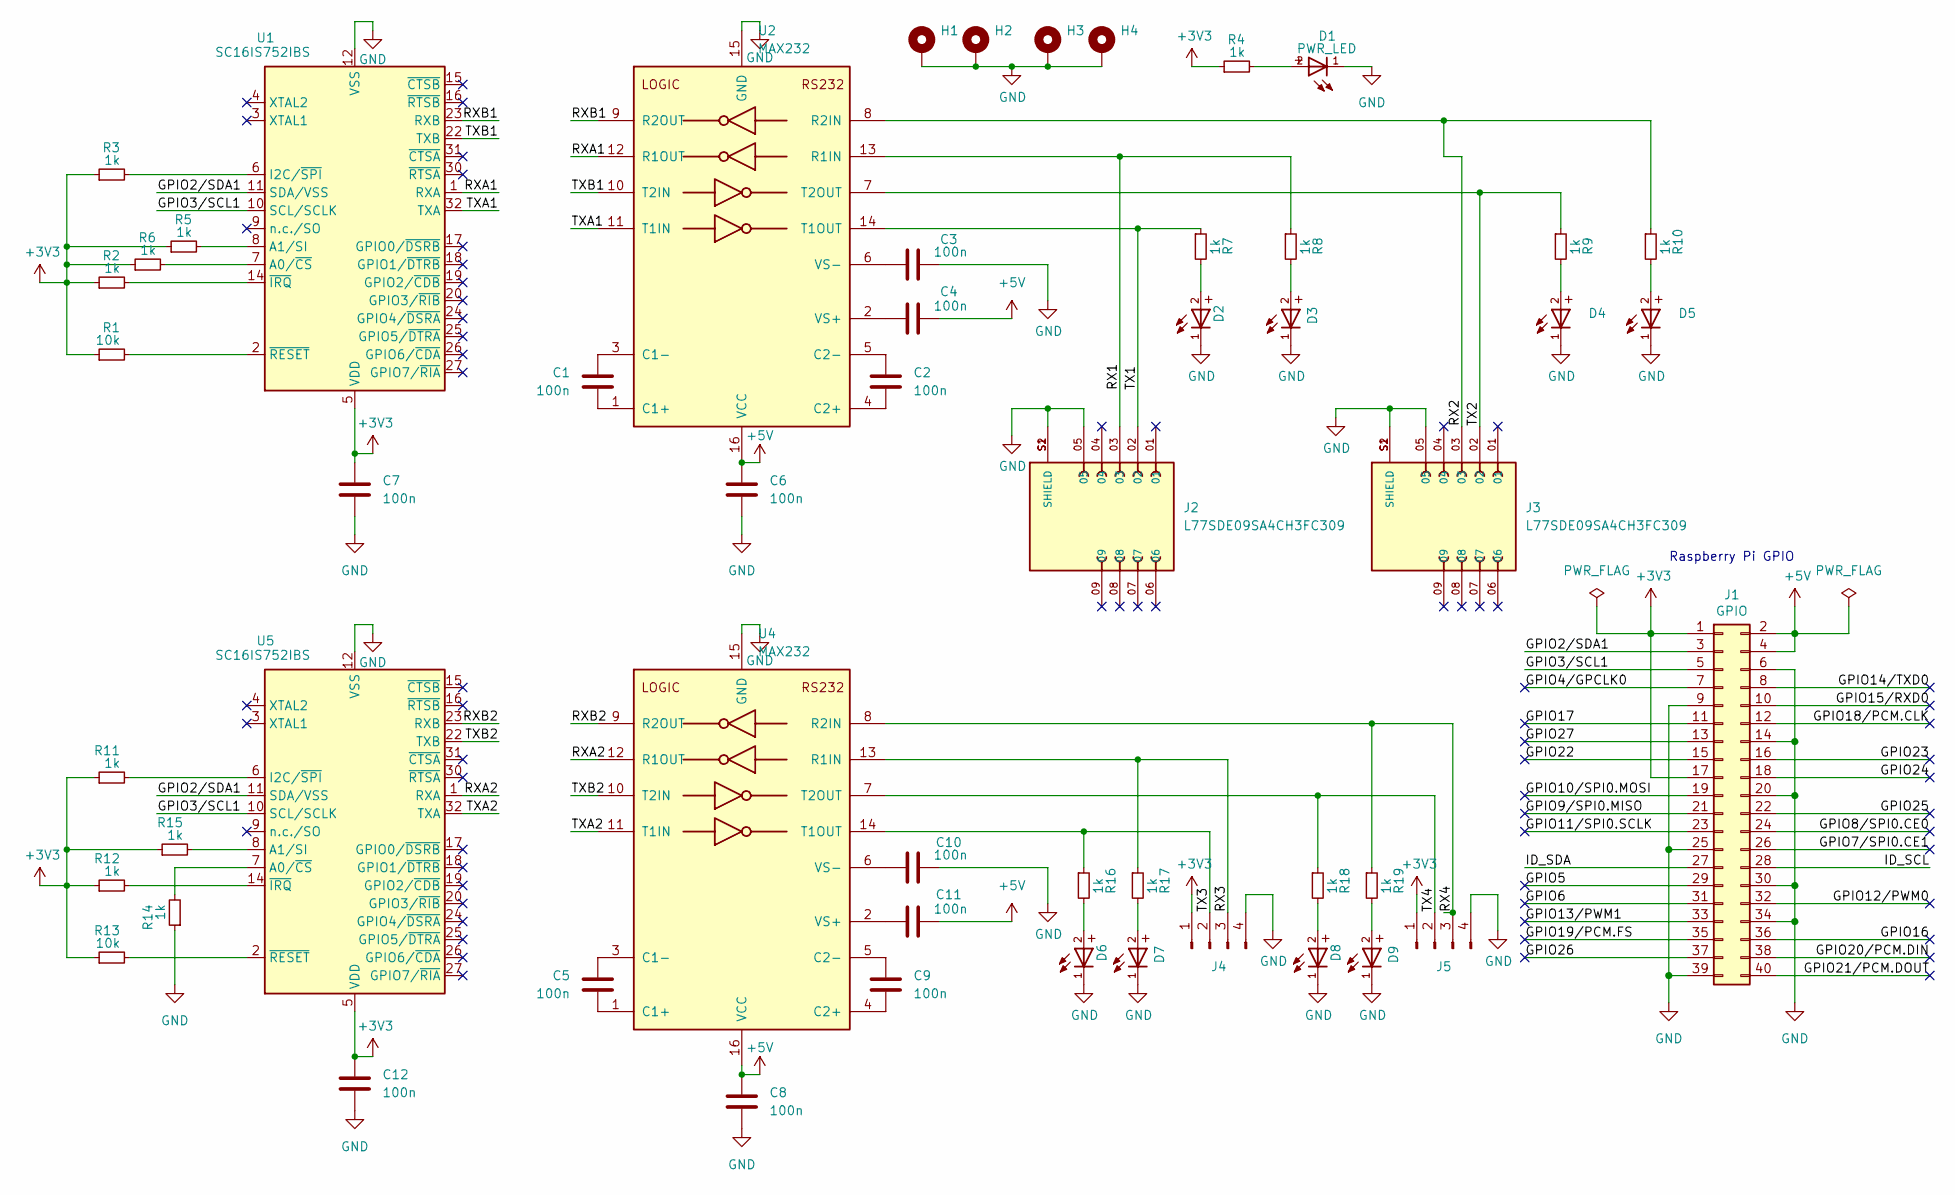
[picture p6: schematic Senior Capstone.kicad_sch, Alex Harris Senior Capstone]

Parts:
C1, C2, C3, C4, C5, C6, C7, C8, C9, C10, C11, C12: 100n; C_0805_2012Metric
D1: PWR_LED; WL-SMCW_0603
D2, D3, D4, D5, D6, D7, D8, D9: WL-SMCW_0603
H1, H2, H3, H4: MountingHole_Pad; MountingHole_2.2mm_M2_ISO7380_Pad_TopBottom
J1: GPIO; PinSocket_2x20_P2.54mm_Vertical
J2, J3: L77SDE09SA4CH3FC309; AMPHENOL_L77SDE09SA4CH3FC309; PARTREV 1
J4, J5: Conn_01x04_Pin; PinHeader_1x04_P2.54mm_Vertical
R1, R13: 10k; R_0805_2012Metric_Pad1.20x1.40mm_HandSolder
R2, R3, R4, R5, R6, R7, R8, R9, R10, R11, R12, R14, R15, R16, R17, R18, R19: 1k; R_0805_2012Metric_Pad1.20x1.40mm_HandSolder
U1, U5: SC16IS752IBS; VQFN-32-1EP_5x5mm_P0.5mm_EP3.1x3.1mm
U2, U4: MAX232; TSSOP-16_4.4x5mm_P0.65mm

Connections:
+3V3: C7.1, C12.1, J1.1, J1.17, J4.1, J5.1, R1.1, R2.1, R3.1, R4.1, R5.1, R6.1, R11.1, R12.1, R13.1, R15.1, U1.5 (VDD), U1.13 (VDD), U1.28 (VDD), U5.5 (VDD), U5.13 (VDD), U5.28 (VDD)
+5V: C4.2, C6.1, C8.1, C11.2, J1.2, J1.4, U2.16 (VCC), U4.16 (VCC)
/GPIO2/SDA1: J1.3, U1.11 (SDA/VSS), U5.11 (SDA/VSS)
/GPIO3/SCL1: J1.5, U1.10 (SCL/SCLK), U5.10 (SCL/SCLK)
/GPIO4/GPCLK0: J1.7
/GPIO5: J1.29
/GPIO6: J1.31
/GPIO7/SPI0.CE1: J1.26
/GPIO8/SPI0.CE0: J1.24
/GPIO9/SPI0.MISO: J1.21
/GPIO10/SPI0.MOSI: J1.19
/GPIO11/SPI0.SCLK: J1.23
/GPIO12/PWM0: J1.32
/GPIO13/PWM1: J1.33
/GPIO14/TXD0: J1.8
/GPIO15/RXD0: J1.10
/GPIO16: J1.36
/GPIO17: J1.11
/GPIO18/PCM.CLK: J1.12
/GPIO19/PCM.FS: J1.35
/GPIO20/PCM.DIN: J1.38
/GPIO21/PCM.DOUT: J1.40
/GPIO22: J1.15
/GPIO23: J1.16
/GPIO24: J1.18
/GPIO25: J1.22
/GPIO26: J1.37
/GPIO27: J1.13
/ID_SCL: J1.28
/ID_SDA: J1.27
/RX1: J2.03, R8.1, U2.13 (R1IN)
/RX2: J3.03, R10.1, U2.8 (R2IN)
/RX3: J4.3, R17.1, U4.13 (R1IN)
/RX4: J5.3, R19.1, U4.8 (R2IN)
/RXA1: U1.1 (RXA), U2.12 (R1OUT)
/RXA2: U4.12 (R1OUT), U5.1 (RXA)
/RXB1: U1.23 (RXB), U2.9 (R2OUT)
/RXB2: U4.9 (R2OUT), U5.23 (RXB)
/TX1: J2.02, R7.1, U2.14 (T1OUT)
/TX2: J3.02, R9.1, U2.7 (T2OUT)
/TX3: J4.2, R16.1, U4.14 (T1OUT)
/TX4: J5.2, R18.1, U4.7 (T2OUT)
/TXA1: U1.32 (TXA), U2.11 (T1IN)
/TXA2: U4.11 (T1IN), U5.32 (TXA)
/TXB1: U1.22 (TXB), U2.10 (T2IN)
/TXB2: U4.10 (T2IN), U5.22 (TXB)
GND: C3.2, C6.2, C7.2, C8.2, C10.2, C12.2, D1.1, D2.1, D3.1, D4.1, D5.1, D6.1, D7.1, D8.1, D9.1, H1.1, H2.1, H3.1, H4.1, J1.6, J1.9, J1.14, J1.20, J1.25, J1.30, J1.34, J1.39, J2.05, J2.S1 (SHIELD), J2.S2 (SHIELD), J3.05, J3.S1 (SHIELD), J3.S2 (SHIELD), J4.4, J5.4, R14.1, U1.12 (VSS), U1.21 (VSS), U1.29 (VSS), U1.33 (VSS), U2.15 (GND), U4.15 (GND), U5.12 (VSS), U5.21 (VSS), U5.29 (VSS), U5.33 (VSS)
unnamed: D1.2, R4.2
unnamed: D2.2, R7.2
unnamed: D3.2, R8.2
unnamed: D4.2, R9.2
unnamed: D5.2, R10.2
unnamed: D6.2, R16.2
unnamed: D7.2, R17.2
unnamed: D8.2, R18.2
unnamed: D9.2, R19.2
unnamed: R6.2, U1.7 (A0/~CS)
unnamed: R5.2, U1.8 (A1/SI)
unnamed: R3.2, U1.6 (I2C/~SPI)
unnamed: R2.2, U1.14 (~IRQ)
unnamed: R1.2, U1.2 (~RESET)
unnamed: C1.2, U2.1 (C1+)
unnamed: C1.1, U2.3 (C1-)
unnamed: C2.2, U2.4 (C2+)
unnamed: C2.1, U2.5 (C2-)
unnamed: C4.1, U2.2 (VS+)
unnamed: C3.1, U2.6 (VS-)
unnamed: C5.2, U4.1 (C1+)
unnamed: C5.1, U4.3 (C1-)
unnamed: C9.2, U4.4 (C2+)
unnamed: C9.1, U4.5 (C2-)
unnamed: C11.1, U4.2 (VS+)
unnamed: C10.1, U4.6 (VS-)
unnamed: R14.2, U5.7 (A0/~CS)
unnamed: R15.2, U5.8 (A1/SI)
unnamed: R11.2, U5.6 (I2C/~SPI)
unnamed: R12.2, U5.14 (~IRQ)
unnamed: R13.2, U5.2 (~RESET)

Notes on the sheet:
Raspberry Pi GPIO

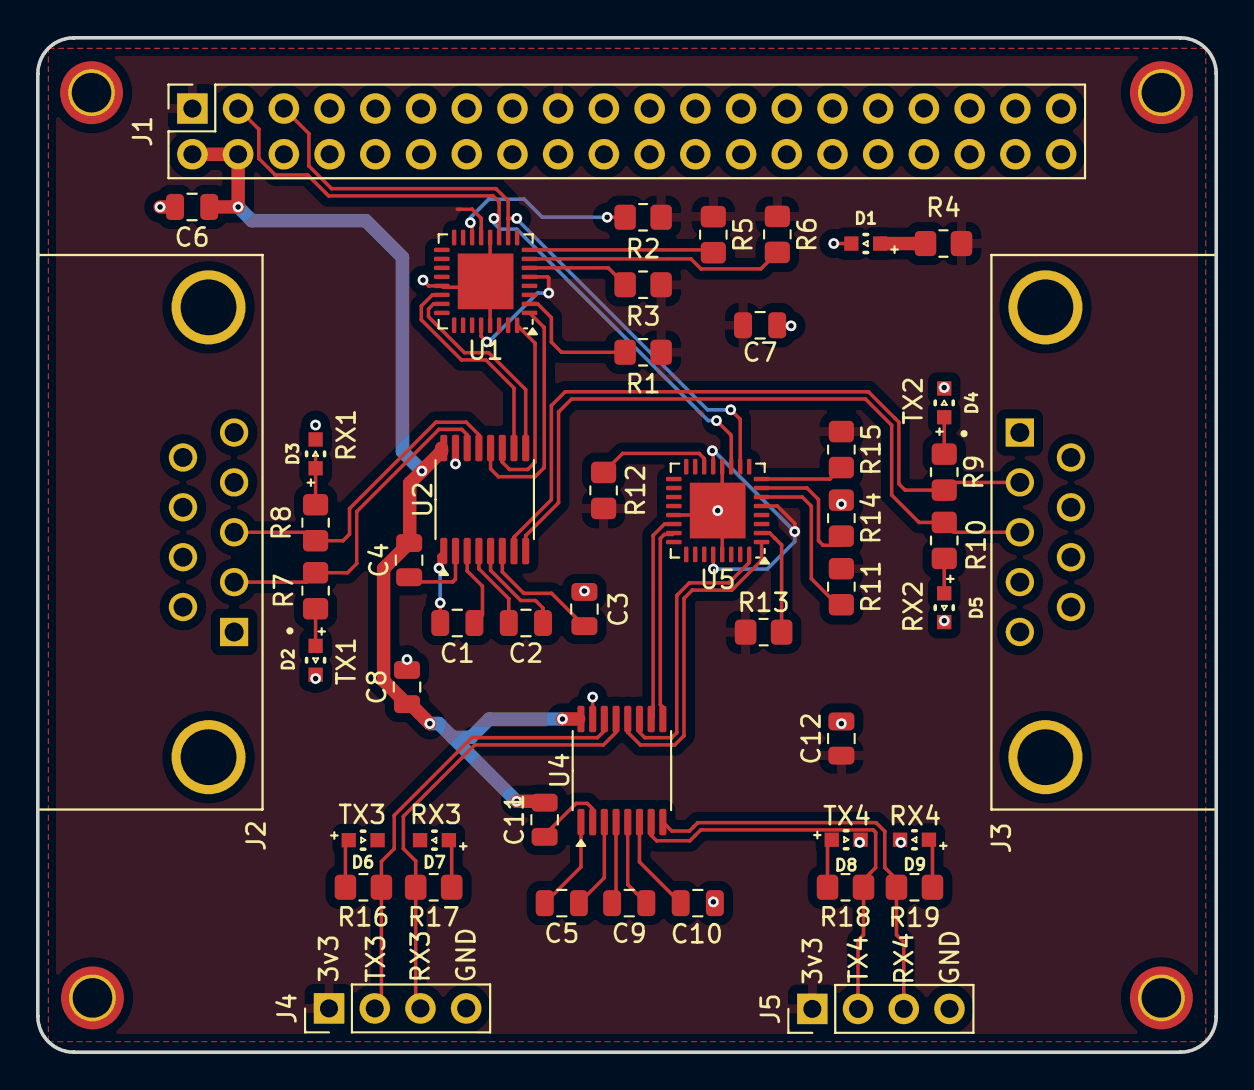
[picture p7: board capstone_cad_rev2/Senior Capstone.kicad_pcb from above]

Board: 2 copper layers, 65.5 x 56.4 mm, 53 parts (0 on the bottom side), 52 nets.

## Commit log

2024-11-20 Serial print loop
2024-11-25 print only
2025-03-03 rev2 and rev3 bom
    [senior_capstone_bom_rev2.xlsx, senior_capstone_bom_rev3.csv]
2025-03-03 replace rev2 bom
    [senior_capstone_bom_rev2.csv]
2025-03-08 capstone rev3 cad files and gerbers
    [GPIB.kicad_sch, Senior Capstone Page 2.kicad_sch, Senior Capstone-B_Cu.gbr, Senior Capstone-B_Mask.gbr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]
2025-03-08 rename files
    [GPIB.kicad_sch, Senior Capstone Page 2.kicad_sch, Senior Capstone-B_Cu.gbr, Senior Capstone-B_Mask.gbr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]
2025-03-08 rename rev2
    [Senior Capstone Page 2.kicad_sch, Senior Capstone.kicad_pcb, Senior Capstone.kicad_sch]
2025-03-08 move boms into folder
    [senior_capstone_bom_rev2.csv, senior_capstone_bom_rev3.csv]
2025-04-07 rev4 files
    [GPIB.kicad_sch, Senior Capstone Page 2.kicad_sch, Senior Capstone.kicad_pcb, Senior Capstone.kicad_sch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]
2025-04-07 rev4 bom
    [capstone rev4 bom.csv]
2025-04-07 move rev4 bom
    [capstone rev4 bom.csv, senior_capstone_bom_rev4.csv]
2025-04-07 capstone rev4 gerbers
    [Senior Capstone-B_Cu.gbr, Senior Capstone-B_Mask.gbr, Senior Capstone-B_Paste.gbr, Senior Capstone-B_Silkscreen.gbr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]
